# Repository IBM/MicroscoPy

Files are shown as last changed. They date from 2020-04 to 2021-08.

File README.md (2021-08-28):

# An open-source MICROSCOPE built using LEGO bricks, 3D-printing, Arduino and Raspberry Pi

Animation

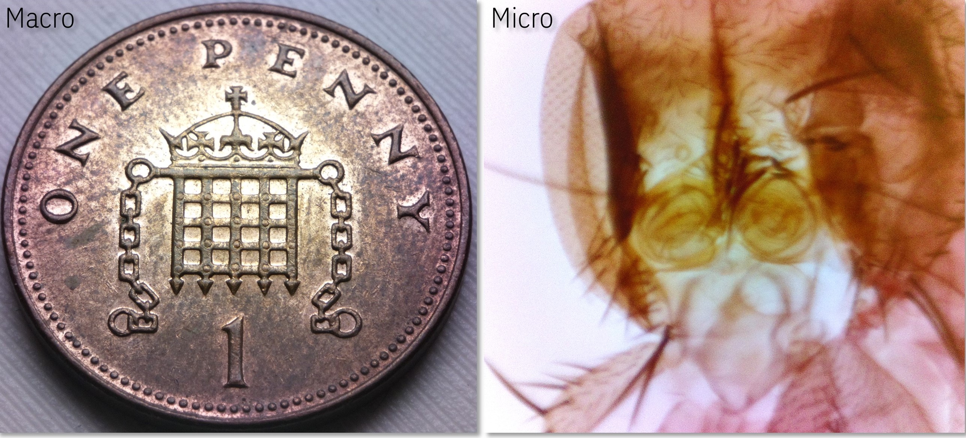
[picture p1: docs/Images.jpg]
Images


Stop-motion

## Key Features

- **Fully motorized:** Camera angle, sample position, magnification and focus can be adjusted precisely using six stepper motors.
- **Modular:** Stages and modules can be arranged in any configuration depending on the application.
- **Versatile:** Uniform illumination guarantees high quality imaging for a variety of samples with reflective or transparent surfaces.  
- **Wide magnification range:** Samples with features from several centimeters to several micrometers can be imaged without changing the objective lens.
- **Low-cost:** The whole assembly costs from $200 to $400 depending on the features and the vendors of the electronic components.  
- The microscope uses a **Raspberry Pi** mini-computer with an **8MP camera** to capture images and videos. Stepper motors and the illumination are controlled using a circuit board comprising an **Arduino microcontroller**, six **stepper motor drivers** and a **high-power LED driver**. All functions can be controlled from a keyboard connected to the Raspberry Pi or a separate custom-built Arduino joystick connected to the mainboard. **LEGO bricks** are used to construct the main body of the microscope to achieve a modular and easy-to-assemble design concept.

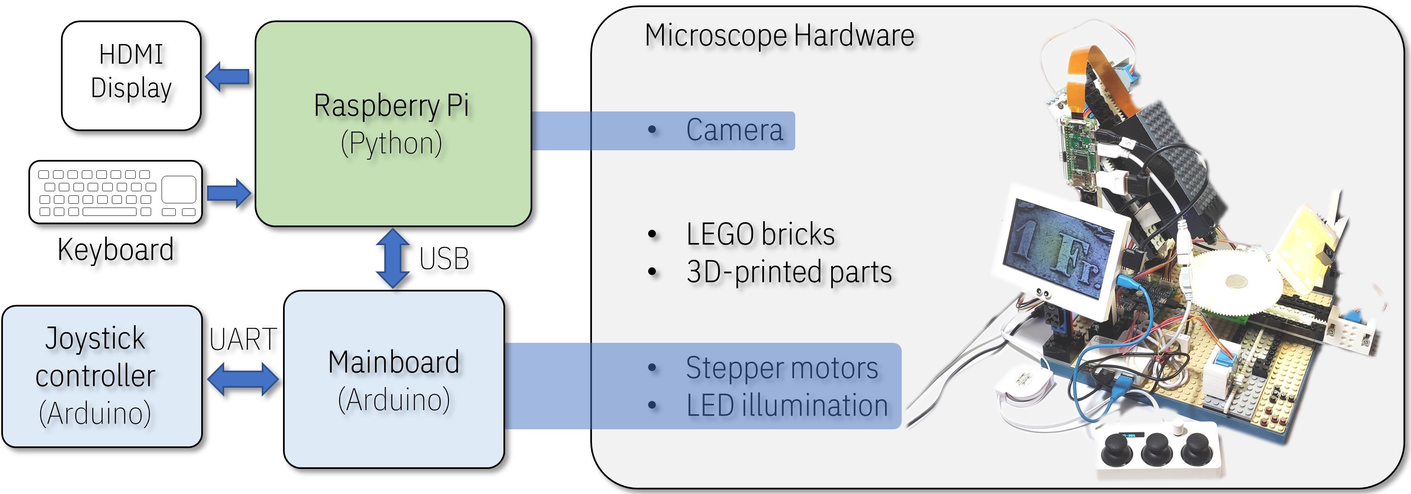
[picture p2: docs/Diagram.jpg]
Diagram


## Assembly instructions

|       [Video (YouTube)](https://youtu.be/PBSYnk9T4o4)        |     [Instructions (PDF)](Instructions.pdf)     |
| :----------------------------------------------------------: | :--------------------------------------------: |
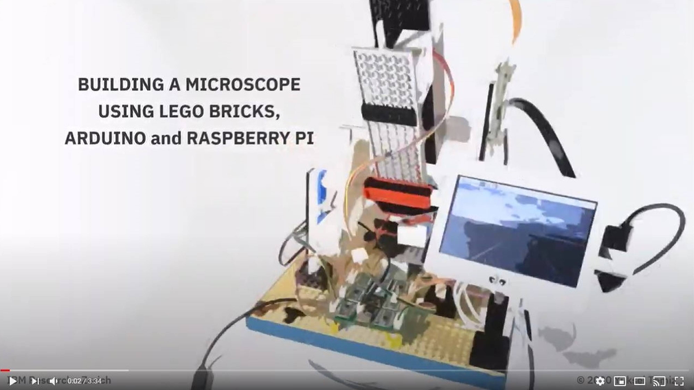
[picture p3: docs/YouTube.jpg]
YouTube (https://youtu.be/PBSYnk9T4o4)
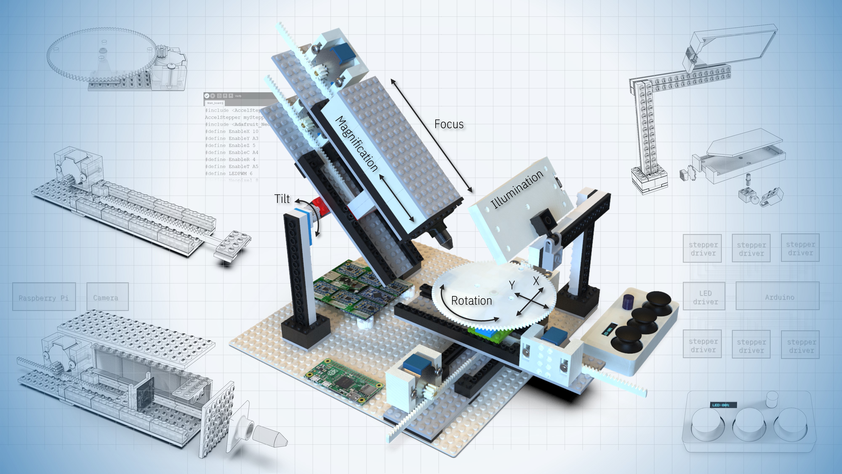
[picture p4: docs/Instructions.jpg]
|  |  |
|  **[Circuit assembly (PDF)](/Circuit/CircuitAssembly.pdf)**  | **[Raspberry Pi HQ camera test](/HQ-camera)**  |
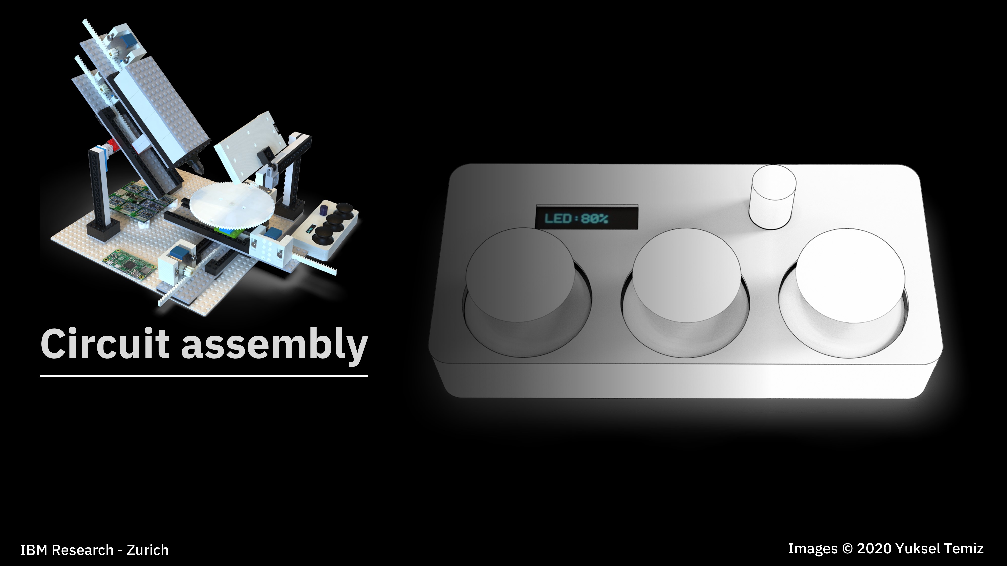
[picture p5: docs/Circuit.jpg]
Circuit
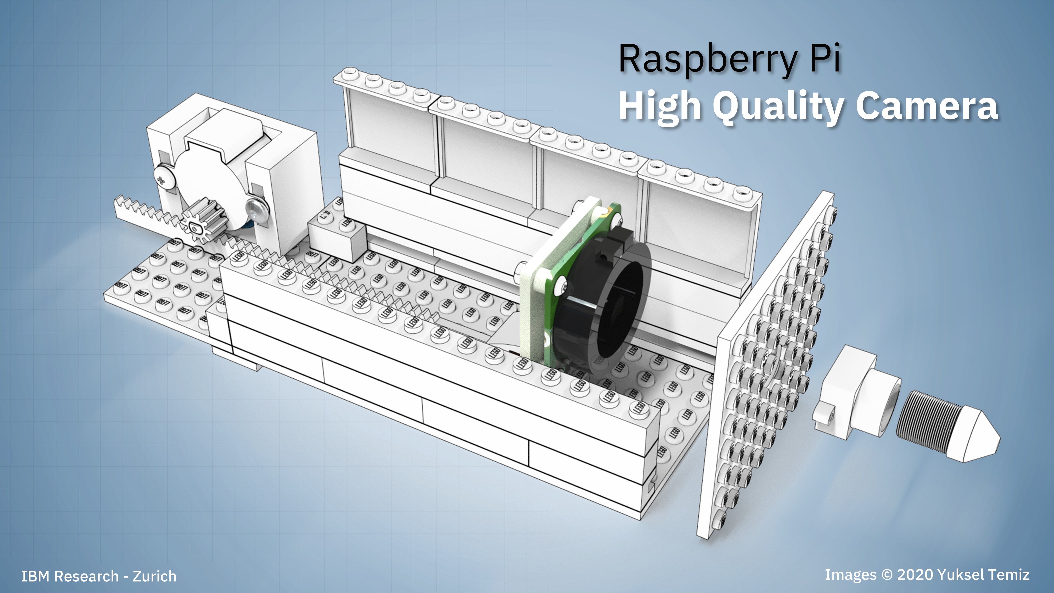
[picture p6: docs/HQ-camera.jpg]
HQ-camera
|  |  |

## Operation principle

The microscope has a simple operation principle based on changing the magnification and the focus by adjusting the relative distances between a **camera**, a single **objective lens** and a **sample**. Briefly, two linear stages with stepper motors are used to adjust these distances for a continuous and wide magnification range. Four additional stepper motors **tilt** the camera module and change the **X-Y position** and **rotation** of the sample. A **uniform light source** illuminates the sample either from an angle *(reflected light)* or from the bottom of the sample *(transmitted light)*. The system can also be used as a *digital water contact angle goniometer* by taking cross-section images of droplets. 

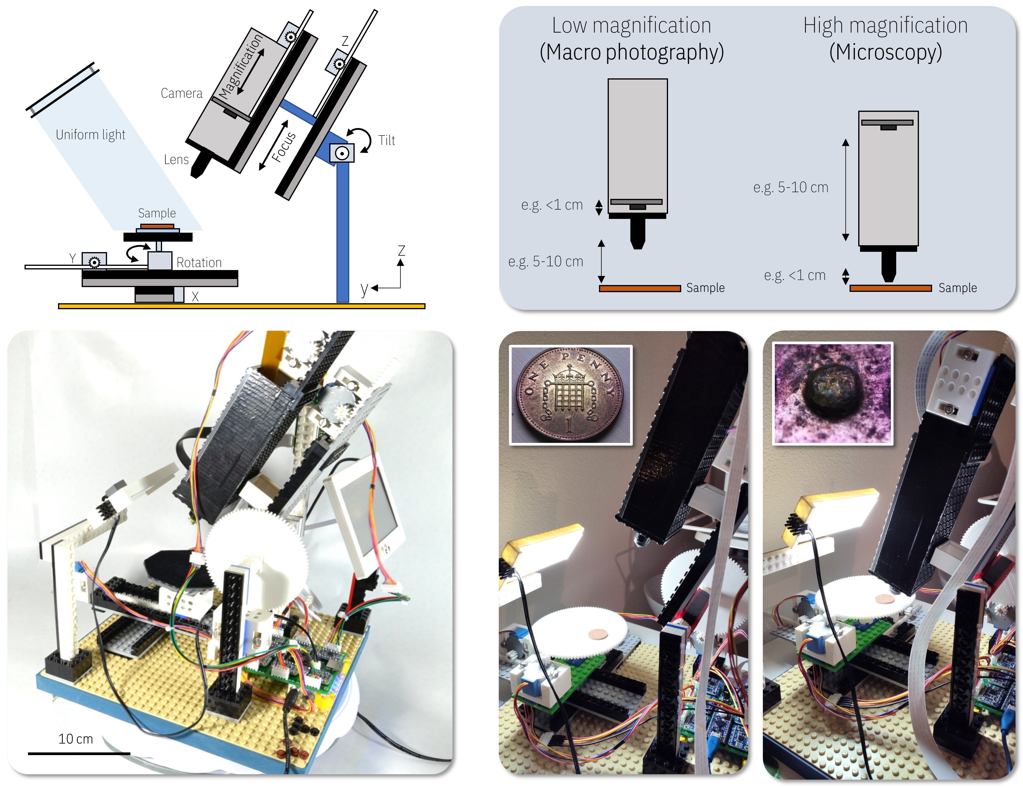
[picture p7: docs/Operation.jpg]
Operation


## Assembly steps

- [Enjoy the YouTube video and get a general idea about the assembly of the microscope.](https://youtu.be/PBSYnk9T4o4) 

- [Follow the detailed instructions provided in the PDF document.](Instructions.pdf)

- [3D print the design files.](#3D-printing)

- [Build the electronic board.](#Electronics)

- [Upload the Arduino code.](#Uploading-the-Arduino-code)

- [Assemble the microscope.](#Final-assembly)

- [Run the Python code.](#Python-Raspberry-Pi)

- [Try different operation modes and enjoy the microscope.](#Basic-operation-modes)

- [Check these instructions if you would like to test the new hiqh quality (HQ) camera](/HQ-camera)

## 3D printing

I assembled the main body of the microscope using individually-purchased [LEGO bricks](https://www.lego.com/en-us/page/static/pick-a-brick). Instead of using motors and gears from LEGO Technic, I designed custom actuators using [FreeCAD](https://www.freecadweb.org/) software and printed them using my personal [3D printer](https://www.creality3d.shop/products/creality3d-ender-3-pro-high-precision-3d-printer). This approach not only lowered the cost of the microscope but also gave me some flexibility in the design and implementation of precise linear and rotary actuators. In principle, the whole structure could be 3D-printed without using any LEGO parts but that would be less modular and more time consuming.  

All STL files for 3D printing and the original FreeCAD files for editing are available in this [folder](https://github.com/IBM/MicroscoPy/tree/master/3D-design-files). You may need to install [FreeCAD Gear workbench](https://wiki.freecadweb.org/Macro_FCGear) to edit the gears. 

:warning: A good quality printing depends on many factors. I optimized the designs after several iterations of printing. If the parts do not match well, some minor modification in the original design file (e.g. enlarging the holes matching to LEGO studs) or polishing/drilling may be required. More information on the printer and slicer settings is given in the [PDF document](Instructions.pdf) (page #72). 

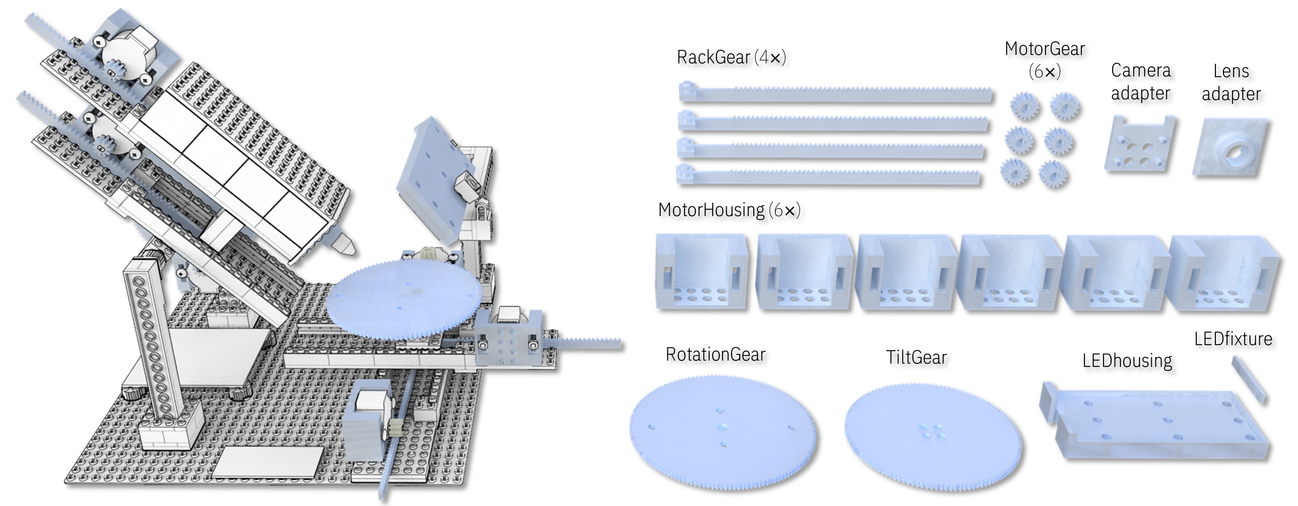
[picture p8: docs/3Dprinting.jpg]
3Dprinting


## Electronics  

:warning: **This part requires some basic knowledge on electronic circuit design and Arduino.**

All design and Gerber files of printed circuit boards (PCBs) are available in this [folder](/Circuit). I designed the PCBs using [DesignSpark PCB software](https://www.rs-online.com/designspark/pcb-software). The list of all components can be found in the [PDF document](Instructions.pdf) (page #71)  

There is also a separate [instruction manual](/Circuit/CircuitAssembly.pdf) giving more details about the assembly of the circuit boards.

The operation of the electronics is straight-forward. I used two Arduino microcontrollers, one for the *mainboard* (essential) and one for the joystick *controller* (optional), to control the stepper motors and the LED illumination of the microscope. In principle, everything could be controlled directly from the Raspberry Pi without using any Arduino microcontroller but I decided to leave testing this option for another time.

:bulb: The joystick controller is optional because the stepper motors and the LED can also be controlled from a keyboard connected to the Raspberry Pi. But having a joystick is fun!

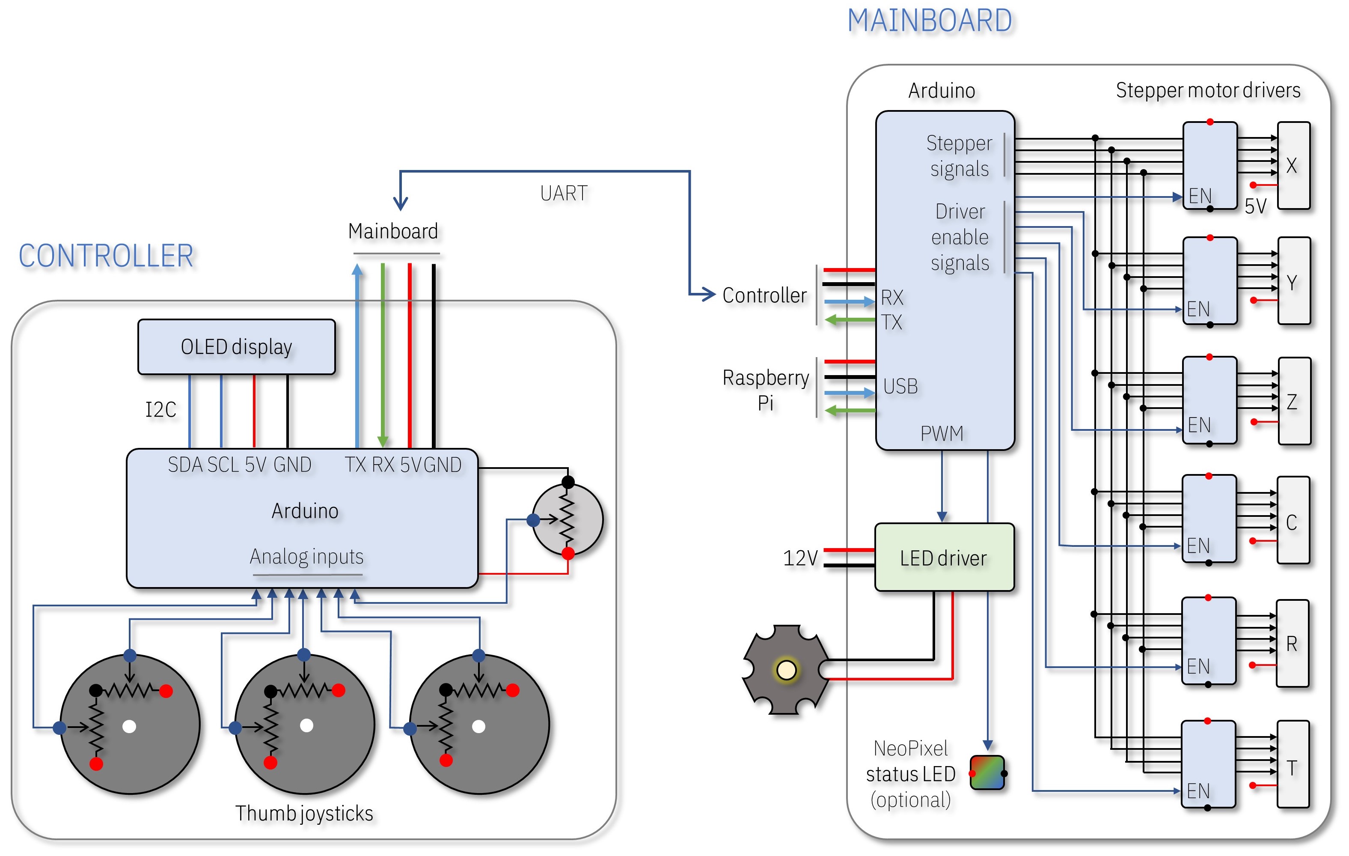
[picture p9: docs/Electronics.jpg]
Electronics


I preferred [Adafruit ItsyBitsy 32u4 5V](https://learn.adafruit.com/introducting-itsy-bitsy-32u4) but any Arduino board with enough number of I/O pins should work. If you want to use the joystick controller, the Arduino boards should support serial (UART) communication because they cannot communicate with each other via their USB ports. 

The Arduino on the *controller* circuit reads the status of three [thumb joysticks](https://www.sparkfun.com/products/9032) (for six stepper motors) and a potentiometer (for the LED intensity) via its analog inputs. The data is sent to the Arduino on the *mainboard* via UART (RX, TX) serial communication. An OLED display on the *controller* can be used to display useful information, like the PWM (pulse-width modulation) intensity of the LED. The Arduino on the *mainboard* receives and processes the incoming data and sends stepper motor signals to the corresponding stepper motor via its respective [motor driver](https://www.adafruit.com/product/3297). Six motor drivers share the same signal pins but only one driver is activated at a time using the *enable* *(EN)* or the *sleep* *(SLP)* pin of the driver. This implementation requires only 10 I/O pins *(4 signal + 6 enable)* instead of 24 *(4 signal x 6 motors)*. It also prevents the heating of the motors when they are idle and limits the current consumption by allowing only one motor running at a time. Alternatively, a motor driver with a built-in indexer with STEP/DIRECTION control can be used to reduce the number of I/O pins but such drivers are more expensive. The data is sent only if there is a change in the joystick position is detected to avoid continuous communication. 

The *mainboard* can be powered from an external 5V wall charger or directly from the USB port of the Raspberry Pi. The latter also allows USB communication between the *mainboard* and the Raspberry Pi to control the stepper motors and the LED intensity from a keyboard. The intensity of the LED is controlled by PWM using a dedicated pin on the Arduino. I recommend keeping the LED off while the Raspberry Pi is booting and then gradually increasing the intensity. The [LED driver](https://www.digikey.com/products/en?keywords=945-1818-5-ND) and the [high-power LED](https://www.digikey.com/products/en?keywords=1672-1161-ND) used in this project required more than 6V for a rated operation. I initially used an external 12V power adapter for the LED but later generated 12V directly from the USB port of the Raspberry Pi using a step-up [DC-DC converter](https://www.banggood.com/DC-DC-Boost-Buck-Adjustable-Step-Up-Step-Down-Automatic-Converter-XL6009-Module-p-1087346.html?rmmds=search&cur_warehouse=CN). In this case, the 5V power adapter should be able to supply enough current for the Raspberry Pi, stepper motors and the LED. I tested the system using a single 5V / 3A supply (original Raspberry Pi 4 power supply or a wall charger). Different configurations may require different power ratings. For example,  if the display is also powered from the same source, then a more powerful 5V source would be needed. [Here](https://www.digikey.com/products/en?keywords=709-GST60A05-P1J) is a good one.  

:warning: The high-power LED gets hot after some time, be cautious. I used a standard aluminum [heat sink](https://www.adafruit.com/product/3083) to help cooling a little bit.  

## Uploading the Arduino code 

- Download the latest version of the [Arduino IDE](https://www.arduino.cc/en/main/software) 
- Install the libraries (Sketch → Include Library → Manage Libraries):
  - [AccelStepper](http://www.airspayce.com/mikem/arduino/AccelStepper/): used to control the stepper motors (mainboard).
  - (Optional) [Adafruit NeoPixel](https://github.com/adafruit/Adafruit_NeoPixel): if you want to have a status LED or nice color effects in the mainboard.
  - (Optional) [Adafruit_GFX](https://github.com/adafruit/Adafruit-GFX-Library) and [Adafruit_SSD1306](https://github.com/adafruit/Adafruit_SSD1306): if you want to have an OLED display in the joystick to show the intensity of the LED illumination.
- Add the board by following these [instructions](https://learn.adafruit.com/introducting-itsy-bitsy-32u4/arduino-ide-setup). 
- Upload the [code(s)](/Arduino). 

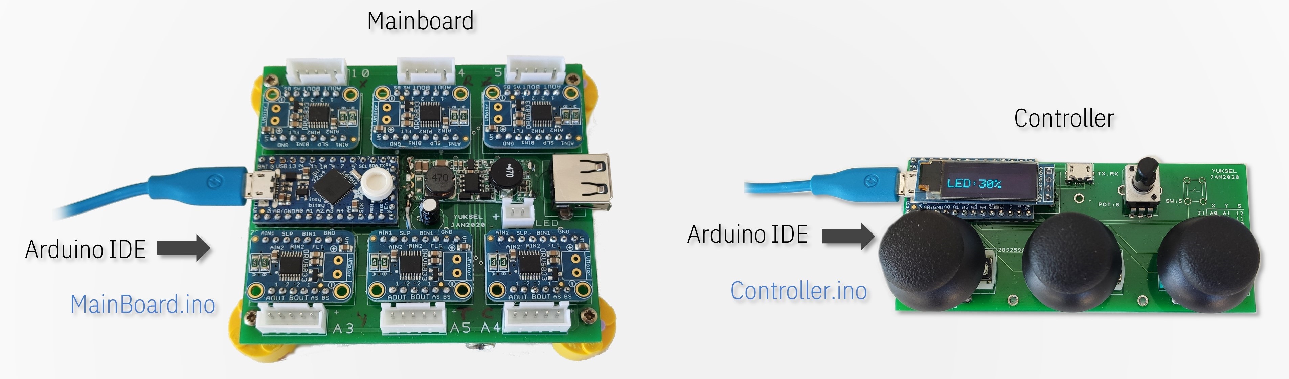
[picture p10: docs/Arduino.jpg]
Arduino


## Final assembly

Follow the detailed instructions given in the [PDF document](Instructions.pdf). Briefly:

- It is important to fix the [32x32 LEGO baseplate](https://www.lego.com/en-us/product/white-baseplate-11010) to a rigid table or support for a good mechanical stability. Rubber dampers or an air cushion can be used to minimize vibrations.  
- Unfortunately it is not possible to create a public shopping basket in the [LEGO shop](https://www.lego.com/en-us/page/static/pick-a-brick), all parts need to be added one by one. I listed the LEGO parts in [this document](List-of-Lego-bricks.pdf) but I recommend buying extra bricks and plates in case you need to change something. 
- Some LEGO parts are needed to be glued permanently for better stability. I provided recommendations in the document based on my experience. In general, it is a good idea to glue a smaller LEGO piece (e.g. 2x2) to a larger one (e.g. 2x4) to have a stronger interlocking while preserving the advantage of LEGO bricks for modularity. 
- After assembling the microscope and connecting all the cables, boot the Raspberry Pi. 
- :warning: Do not forget to enable the camera from the Raspberry Pi configuration (Preferences → Raspberry Pi configuration → Interfaces → Camera Enabled → Reboot)  as explained [here](https://projects.raspberrypi.org/en/projects/getting-started-with-picamera). 

Assembly

## Python-Raspberry Pi

I wrote a simple [program](/Python) in Python 3 to control the microscope, modify camera settings and take photos and videos from keyboard. The code allows changing almost all camera settings using keyboard shortcuts. The speed and the direction of the stepper motors and the LED intensity can also be controlled from the keyboard independently from the joystick controller.

The code requires following dependencies: 

- [EasyGUI](https://pythonhosted.org/easygui/index.html): to generate simple message boxes and select the folder where the images are saved
- [pySerial](https://pythonhosted.org/pyserial/): to communicate with the Arduino via USB
- [pynput](https://pypi.org/project/pynput/): to monitor keyboard inputs

There are two important parameters in the program to be changed according to your configuration:

**HighResolution:** 

- **True** for (3280x2464), tested with Raspberry Pi 4.
- **False** for (1920x1080), tested with Raspberry Pi 3 and Zero. 

**KeyboardControl:** 

- **True** if the Arduino mainboard is connected to the Raspberry Pi via USB.
- **False** if the mainboard is not connected and powered from an external 5V supply 

**Finally, launch the program from the terminal and enjoy the microscope:** 

```bash
python3 /home/pi/MicroscoPy.py 
```

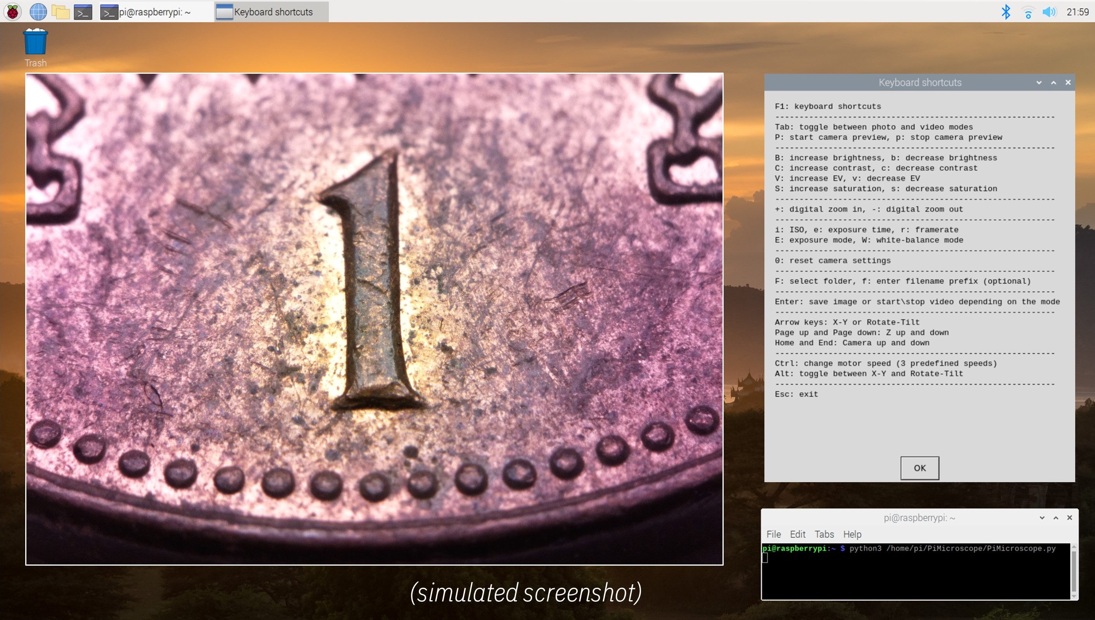
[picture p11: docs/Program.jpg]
Program


## Basic operation modes

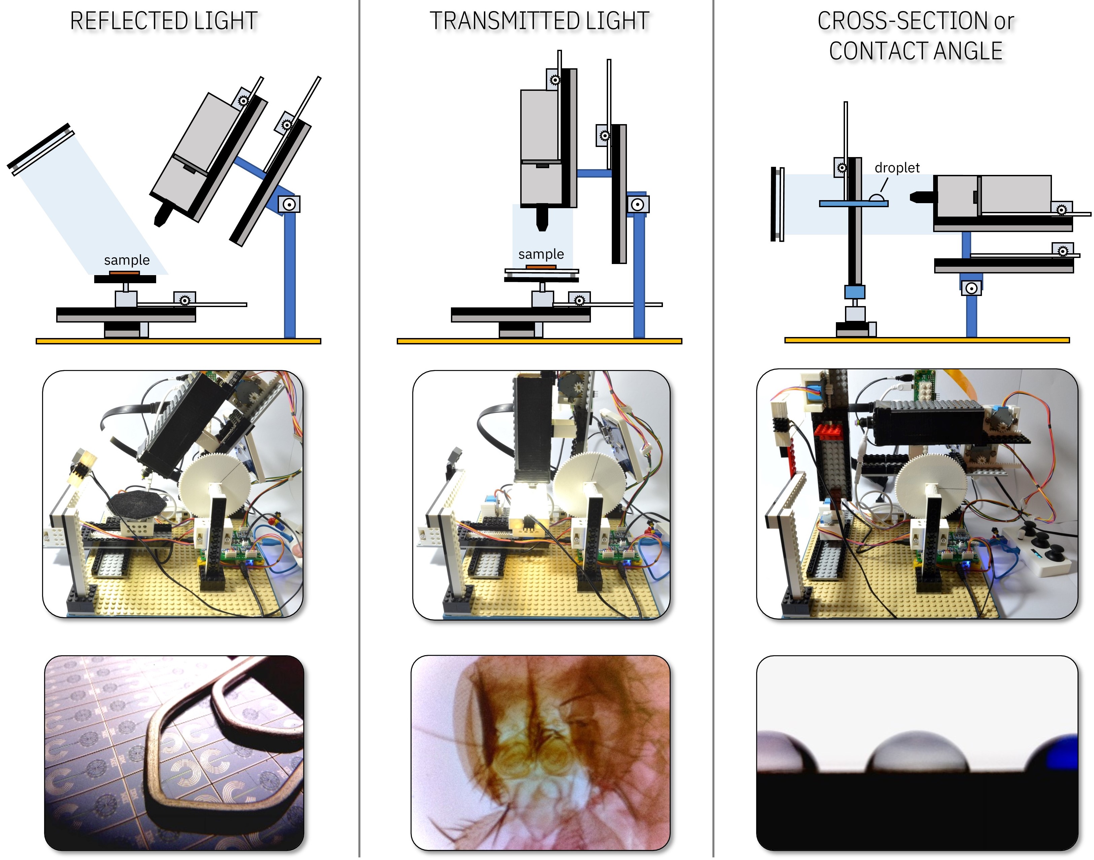
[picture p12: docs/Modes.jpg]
Modes


## Media coverage

[IEEE Spectrum](https://spectrum.ieee.org/geek-life/hands-on/build-a-sophisticated-microscope-using-lego-3d-printing-arduinos-and-a-raspberry-pi): "Build A Sophisticated Microscope Using Lego, 3D Printing, Arduinos, and a Raspberry Pi"

[IBM - Medium article](https://medium.com/@IBMResearch/ibm-open-sources-300-fully-functional-lego-microscope-design-248a6cdc81bf): "IBM open sources $300 fully-functional LEGO®microscope design"

[Futurism](https://futurism.com/engineer-published-scientific-papers-lego-microscope): "This Engineer Published Scientific Papers Using a Lego Microscope"

## License

This project uses the [Apache License Version 2.0](LICENSE) software license. 

Separate third-party libraries used in Arduino and Python codes are licensed by their respective providers pursuant to their own separate licenses. 

## About

**The microscope is not currently available for purchase in kit or built form.** 

Copyright 2021 [Yuksel Temiz](https://www.linkedin.com/in/yukseltemiz/)

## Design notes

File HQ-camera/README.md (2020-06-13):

# Raspberry Pi High Quality (HQ) camera test

This folder is dedicated to Raspberry Pi's new [HQ camera](https://www.raspberrypi.org/products/raspberry-pi-high-quality-camera/). 

The new camera gives a better quality imaging but it is 50% larger thus it requires a larger Lego housing, which challenges the tilting mechanism. The improvement is marginal for many cases because the performance of this microscope is anyway limited by other factors, like the low-cost objective lens. 

Overall, I think it is NOT worth the extra effort and cost unless a completely new microscope architecture with a more stable tilting mechanism and a better quality lens is designed.

Follow these detailed [instructions](Instructions_HQ.pdf) if you would like to try yourself. 

**Note:** Use the modified Python code (**MicroscoPy_HQ.py**) in this folder for the best resolution.

HQ-camera

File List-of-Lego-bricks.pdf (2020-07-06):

List of Lego bricks used in the prototypes.

Some bricks may not be available in your country, but there are always alternative implementations in the world of Lego bricks. Also, there are probably many different ways of building a similar or better modules than I designed.
So, use your imagination and order extra bricks from different kinds in case you may want to modify something.

Keep in mind that some parts are required to be glued to a bigger piece for better mechanical stability.

I appreciate if you also keep in mind that this is a research prototype originated from my hobby, not a product.
There are probably many things that could have been done better, so consider the documents as a guideline but not as a product manual. Please let me know if you spot an error or have suggestions for improvements.

### https://www.lego.com/en-us/page/static/pick-a-brick

Module | Lego design name | Lego design ID | Quantity per unit | Quantity total | Purpose | Page # in the instructions | Comments
Base | 1 unit
| Baseplate 32x32 | | 1 | 1 | base | 32 | needs to be fixed to a rigid substrate
Linear actuators | 4 units
| PLATE 6X16 | 3027 | 1 | 4 | main plate for the linear stage | 5
| SLIDING PIECE 1X4 | 2653 | 8 | 32 | sliding guides on the sides | 5
| PLATE 1X2 WITH SLIDE | 32028 | 2 | 8 | sliding pieces | 7
| PLATE 2X4 | 3020 | 1 | 4 | moving plate | 7
| PLATE 2x6 | 3795 | 1 | 4 | mechanical stability | 6
| PLATE 6x8 | 3036 | 1 | 4 | motor plate | 6
| BRICK CORNER 1X2X2 | 2357 | 2 | 8 | mechanical stability | 6
| PLATE 2X4 | 3020 | 1 | 4 | motor Lego adapter | 9
Camera module | 1 unit | | | | | | in addition to one linear stage
| WALL ELEMENT 1X4X3, ABS | 60581 | 8 | 8 | sidewalls | 18
| PLATE 6X16 | 3027 | 1 | 1 | top cover | 19
| ANGLE PLATE 1X2 / 2X4 | 21731 | 1 | 1 | top cover connection | 19
| ANGULAR PLATE 1.5 BOT. 1X2 2/2 | 99207 | 1 | 1 | camera Lego adapter | 15
| PLATE 6x6 | 3958 | 1 | 1 | front cover | 19
| FRAME 1X4X3 | 60594 | 2 | 2 | Camera-Z connection spacer | 58
| PLATE 2X4 | 3020 | 1 | 1 | Camera-Z connection spacer | 57
Rotaty stage (option 1) | 1 unit
| 10x10 OCTOGONAL PLATE | 89523 | 1 | 1 | stage | 25
| PROFILE BRICK Ø15.83 W. CROSS | 92947 | 1 | 1 | connection to the motor | 25
| PLATE 2X4 | 3020 | 1 | 1 | motor Lego adapter | 25
Rotaty stage (option 2) | 1 unit | | | | | | preferred, better precision
| PLATE 4X12 | 3029 | 1 | 1 | stage base | 26
| NOSE CONE SMALL 1X1 | 59900 | 1 | 1 | pivot | 26
| LIGHT SWORD - BLADE | 21462 | 1 | 1 | pivot rod | 26
| NOSE CONE 2X2X2 | 14918 | 1 | 1 | support for the rod | 26
| PLATE 2X4 | 3020 | 1 | 1 | mechanical stability | 26
| PLATE 2X4 | 3020 | 1 | 1 | motor Lego adapter | 25
Vertical supports | 3 units | | | | | | tilt mechanism and illumination
| BRICK 1X16 | 2465 | 2 | 6 | pillar | 30
| PLATE 2X16 | 4282 | 1 | 3 | pillar | 30
| FRAME PLATE 4X4 | 64799 | 1 | 3 | pillar support | 30
| ANGULAR PLATE 1.5 BOT. 1X2 2/2 | 99207 | 1 | 3 | connection | 30
| BRICK CORNER 1X2X2 | 2357 | 4 | 12 | connection | 30
| PLATE 1X4 | 3710 | 4 | 12 | connection | 30
| PLATE 1x2 | 3023 | 4 | 12 | connection | 30
Tilt mechanism | 1 unit
| TECHNIC BRICK 1X2, Ø4.9 | 3700 | 2 | 2 | camera stage | 31
| CONN.BUSH W.FRIC./CROSSALE | 43093 | 2 | 2 | camera stage | 31
| PLATE 2X8 | 3034 | 2 | 2 | camera stage | 31
| BRICK 2X6 | 44237 | 1 | 1 | camera stage | 31
| PLATE 2X4 | 3020 | 3 | 3 | mechanical stability | 34-37
| PLATE 2X4 | 3020 | 1 | 1 | motor Lego adapter | 34-37
| PROFILE BRICK Ø15.83 W. CROSS | 92947 | 5 | 5 | spacer | 34-37
| TURN PLATE 2X2, LOWER PART | 3680 | 2 | 2 | rotation | 34-37
| TURN PLATE 2X2, UPPER PART | 3679 | 2 | 2 | rotation | 34-37
Illumination | 1 unit | | | | | | in addition to one vertical support
| CONN.BUSH W.FRIC./CROSSALE | 43093 | 4 | 4 | connection to the stage | 42-44 | for bottom illumination
| BRICK 1X16 | 2465 | 2 | 2 | horizontal connection | 43
| PLATE 2X16 | 4282 | 1 | 1 | horizontal connection | 43
| BRICK 2X2 W. BALL Ø 10.2 | 57909 | 1 | 1 | hinge | 43 | for top illumination
| BRICK 2X2 W. CUP FOR BALL | 92013 | 1 | 1 | hinge | 43 | for top illumination

OPTIONAL
HQ camera (experimental) | 1 unit | | | | | | Optional. Refer to the Instructions_HQ.pdf
linear actuator | PLATE 8x16 | 92438 | 1 | 1 | main plate | 4
linear actuator | PLATE 6x8 | 3036 | 1 | 1 | motor plate | 4
linear actuator | PLATE 2x8 | 3034 | 1 | 1 | mechanical stability | 4
linear actuator | PLATE 2x6 | 3795 | 1 | 1 | moving plate | 4 | same as camera v2
linear actuator | PLATE 1X2 WITH SLIDE | 32028 | 2 | 2 | sliding pieces | 4 | same as camera v2
linear actuator | BRICK CORNER 1X2X2 | 2357 | 2 | 2 | mechanical stability | 4 | same as camera v2
linear actuator | PLATE 2X4 | 3020 | 1 | 1 | motor Lego adapter | 4 | same as camera v2
linear actuator | SLIDING PIECE 1X4 | 2653 | 8 | 8 | sliding guides on the sides | 4 | same as camera v2
camera module | ANGULAR PLATE 1.5 BOT. 1X2 2/2 | 99207 | 1 | 1 | camera Lego adapter | 6 | same as camera v2
camera module | PLATE W. BOW 2X2X2/3 | 15068 | 1 | 1 | mechanical stability | 7
camera module | WALL ELEMENT 1X4X3, ABS | 60581 | 8 | 8 | sidewalls | 9 | same as camera v2
camera module | BRICK 1X16 | 2465 | 4 | 4 | additional height | 9
camera module | ANGLE PLATE 1X2 / 2X4 | 21731 | 1 | 1 | top cover connection | 10 | same as camera v2
camera module | PLATE 8X16 | 92438 | 1 | 1 | top cover | 10
camera module | PLATE 8X8 | 41539 | 1 | 1 | front cover | 10
tilt mechanism | PLATE 4X8 | 3035 | 2 | 2 | camera stage top and bottom plate | 13 | wider stage
tilt mechanism | TECHNIC BRICK 1X2, Ø4.9 | 3700 | 2 | 2 | camera stage | 13 | same as camera v2
tilt mechanism | CONN.BUSH W.FRIC./CROSSALE | 43093 | 2 | 2 | camera stage | 13 | same as camera v2
tilt mechanism | BRICK 1X8 | 3008 | 2 | 2 | camera stage | 13
tilt mechanism | PLATE 2X6 | 3795 | 1 | 1 | camera stage | 13

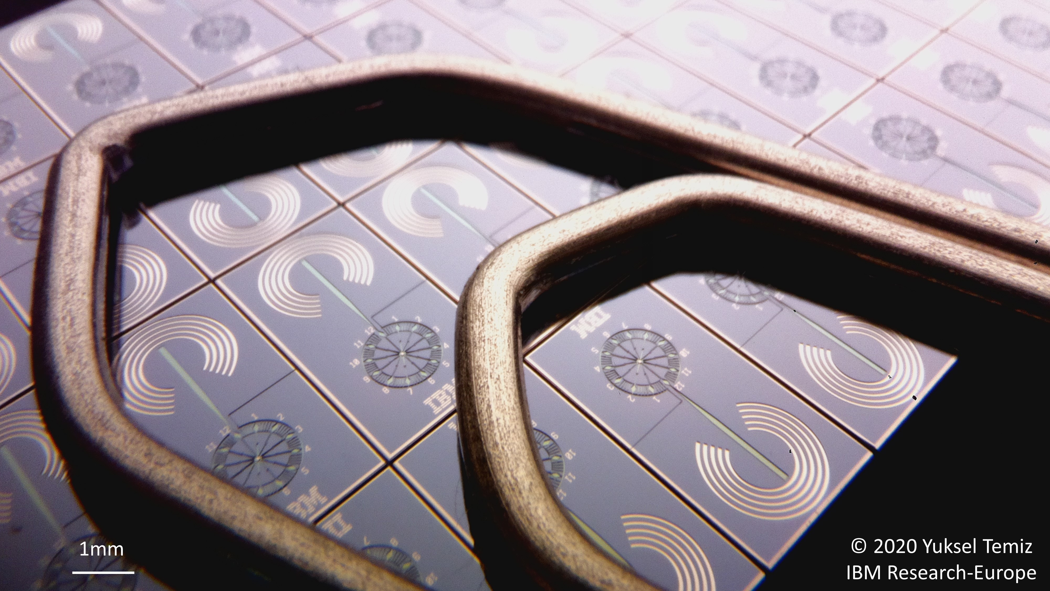
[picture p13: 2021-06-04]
Image-examples/Microfluidic-clock_and_paper-clip.jpg

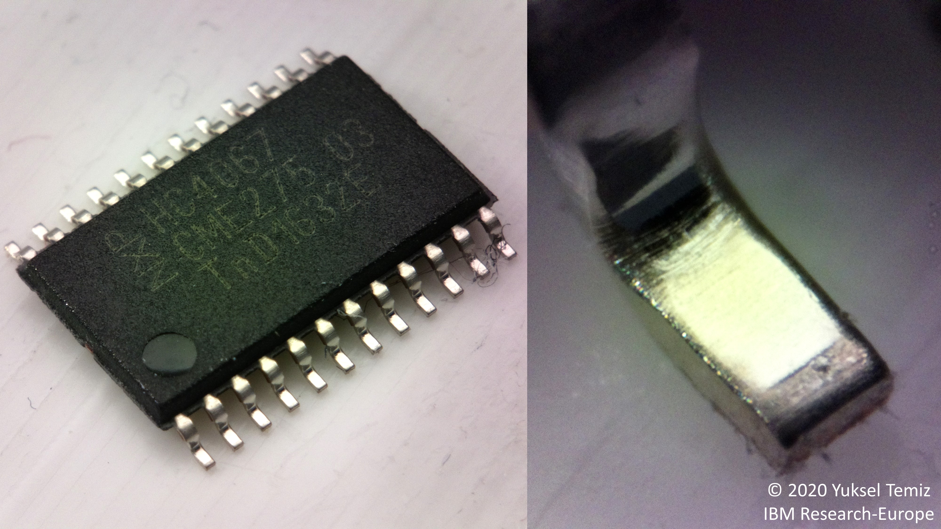
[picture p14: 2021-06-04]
Image-examples/Integrated-Circuit.jpg

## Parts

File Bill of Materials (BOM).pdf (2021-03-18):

# Bill of materials

I tem | Total price ($) | Remarks
LEGO bricks (https://www.lego.com/en-us/page/static/pick-a-brick) | ~60 | I recommend buying extra bricks in different sizes.
Raspberry Pi (https://www.raspberrypi.org/products/) | 10-50 | Any model works.
Raspberry Pi camera (https://www.raspberrypi.org/products/camera-module-v2/) | 25
Camera flex cable (https://www.adafruit.com/product/1731) | 3 | A long cable (>40cm) is preferred if the Raspberry Pi cannot be placed closer to the camera.
Magnifying lens (https://www.aliexpress.com/i/32879460954.html) | 10 | M12 thread
Micro SD card (https://www.raspberrypi.org/documentation/installation/sd-cards.md) | 10 | Raspberry Pi operating system. Minimum 16GB is recommended.
HDMI display (https://www.adafruit.com/product/2260) | 50-150 | Optional if an HDMI display is already available. The price varies depending on the size and the model.
Arduino board (https://www.adafruit.com/product/3677) x2 | 20 | One for the mainboard, one for the controller. Any Arduino board with enough number of IO pins should work.
Stepper motor driver (https://www.adafruit.com/product/3297) x6 | 30 | Any other 5V compatible driver should work. Microstepping was not needed in this project.
Stepper motor (https://www.banggood.com/28BYJ-48-5V-4-Phase-DC-Gear-Stepper-Motor-DIY-Kit-p-1553617.html?rmmds=search&cur_warehouse=CN) x6 | 15 | 28BYJ-48, 5V, 1/64 gear ratio
JST-XH 5P 4S cables (https://www.ebay.com/itm/JST-XH-5P-4S-Li-PO-Balance-Charging-Wire-Extension-22AWG-20cm-Adapter-Lead-x-5/122329707748) | 7 | A few of these cables are required the extend the default cable of the stepper motor (28BYJ-48)
High-power LED (https://www.digikey.com/products/en?keywords=1672-1161-ND) | 4
High-power LED driver (https://www.digikey.com/products/en?keywords=945-1818-5-ND) | 14
Light diffuser (https://www.adafruit.com/product/1621) | 3 | An LED backlight module is modified by replacing the low-power LED by a high-power one
Potentiometer (https://www.adafruit.com/product/4133) | 1 | LED intensity control using pulse-width modulation.
Thumb joysticks (https://www.sparkfun.com/products/9032) x3 | 12 | Three joysticks for X, Y, Z, Camera, Tilt, and Rotation.
5V power supply (https://www.raspberrypi.org/products/type-c-power-supply/) | 20 | At least 3A is preferred. A more powerful supply may be needed if the display is also powered from the same supply.
DC-DC converter for the LED (https://www.banggood.com/USB-Boost-Line-Power-Supply-5V-To-12V-Power-Line-1A-Power-Cord-p-1268454.html) | 3 | 5V to 12V converter for the LED (note: I do not recommend using Raspberry Pi’s USB output for the LED, you can use a separate 12V power supply or use this converter with a standard 5V phone charger)
DC barrel connector (LED) (https://www.digikey.com/en/products/detail/cui-devices/PJ-002A/96962?s=N4IgTCBcDaIMYAcC0AGFYCGSB2ATEAugL5A) | 1 | Connector for the 12V input (LED)
OLED display (https://www.banggood.com/0_91-Inch-128x32-IIC-I2C-Blue-OLED-LCD-Display-DIY-Oled-Module-SSD1306-Driver-IC-DC-3_3V-5V-p-1140506.html?rmmds=search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) | 3 | Displays the LED intensity or any other information on the controller.
USB connector (https://www.digikey.com/products/en?keywords=UE27AC5410H-ND) (type A) | 0.5 | Connection between the mainboard and the controller (mainboard side).
USB connector (https://www.digikey.com/products/en?keywords=609-4616-1-ND) (micro) | 0.5 | Connection between the mainboard and the controller (controller side).
JST XH connector set (https://www.banggood.com/40-Sets-JST-2_5mm-XH-2P-3P-4P-5Pin-Male-Female-Housing-Connector-with-Crimps-p-1180083.html?rmmds=search&cur_warehouse=CN) | 5 | Connectors for the stepper motors and the LED
OVERALL TOTAL | ~300

## - The prices and the links are for exemplary components that

were used in this prototype.

## - Any other compatible model

should work in principle.

## - The total price varies significantly depending on the vendor and the model. For example, the type of the Raspberry Pi and the display makes a big difference in the

price.

## - The cost of 3D-printed parts is

not included.

## - There are also a few other accessories needed, like USB

cables, an HDMI cable,

## optionally a mouse and a

keyboard, an ON/OFF switch,

## screws and nuts, and printed

circuit boards (PCBs).

IBM Research - Zurich | Images © 2020 Yuksel Temiz

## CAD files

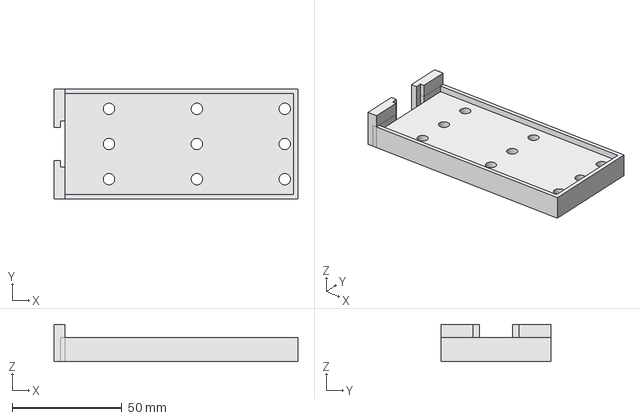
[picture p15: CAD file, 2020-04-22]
3D-design-files/FreeCAD/9-LEDhousing.FCStd
111.0 x 50.0 x 17.0 mm

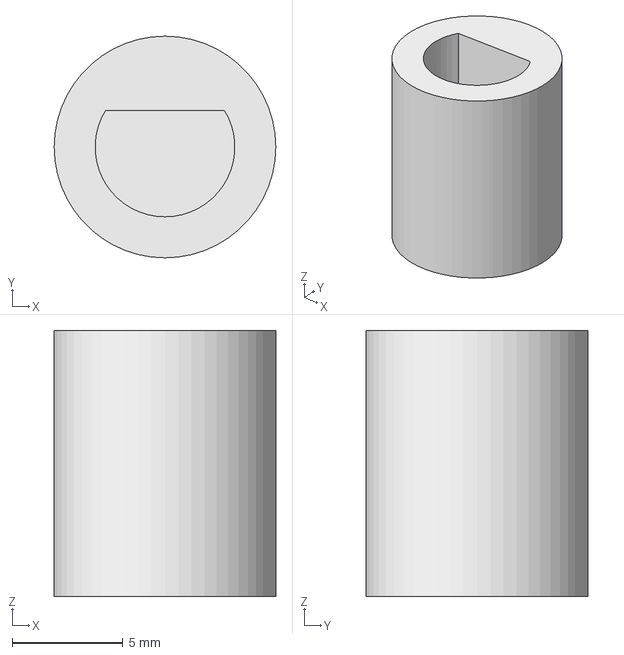
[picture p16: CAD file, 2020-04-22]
3D-design-files/FreeCAD/Joystick Controller/Controller knob.FCStd
10.0 x 10.0 x 12.0 mm

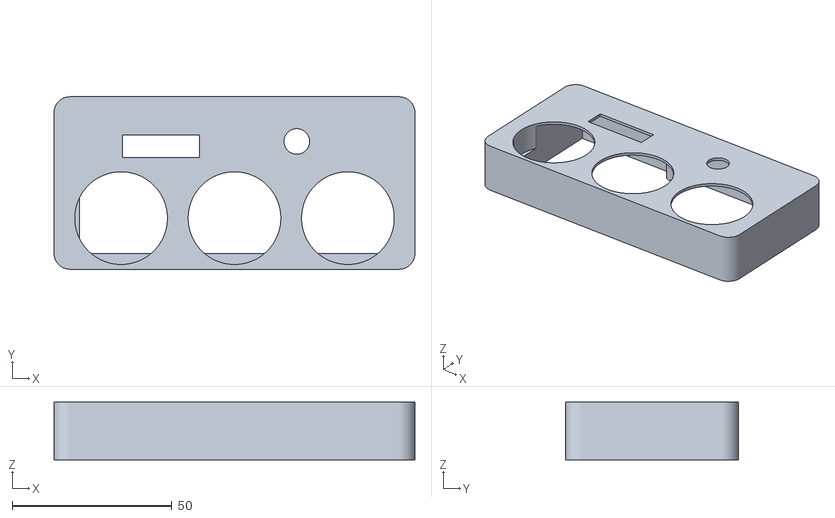
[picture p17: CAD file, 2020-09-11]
3D-design-files/STL/11-ControllerHousing.stl
113.0 x 54.0 x 18.0

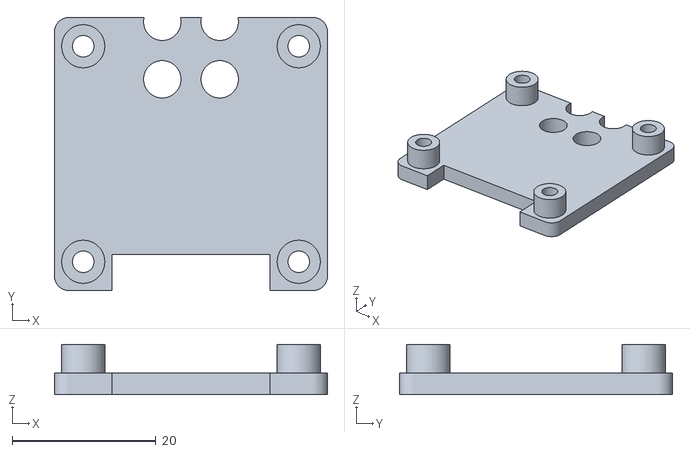
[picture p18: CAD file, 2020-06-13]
HQ-camera/CameraAdapter_HQ.stl
38.0 x 38.0 x 7.00

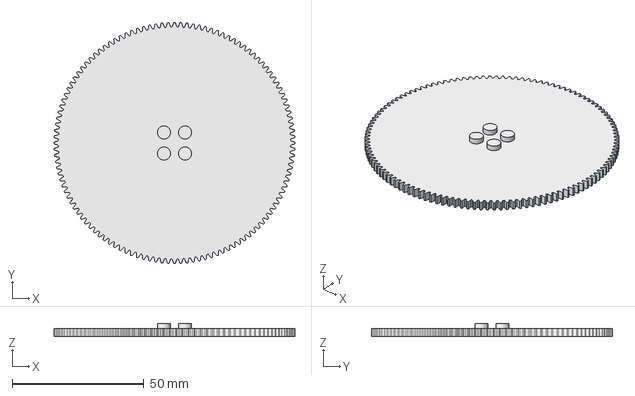
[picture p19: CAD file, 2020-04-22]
3D-design-files/FreeCAD/8-TiltGear.FCStd
91.5 x 91.5 x 4.90 mm

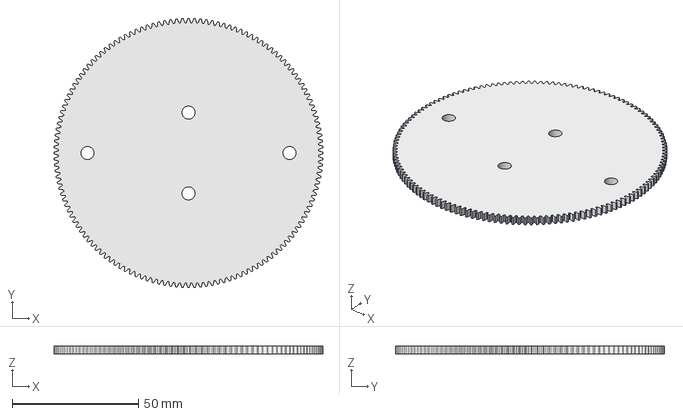
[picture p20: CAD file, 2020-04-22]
3D-design-files/FreeCAD/7-RotationGear.FCStd
106.5 x 106.5 x 3.00 mm

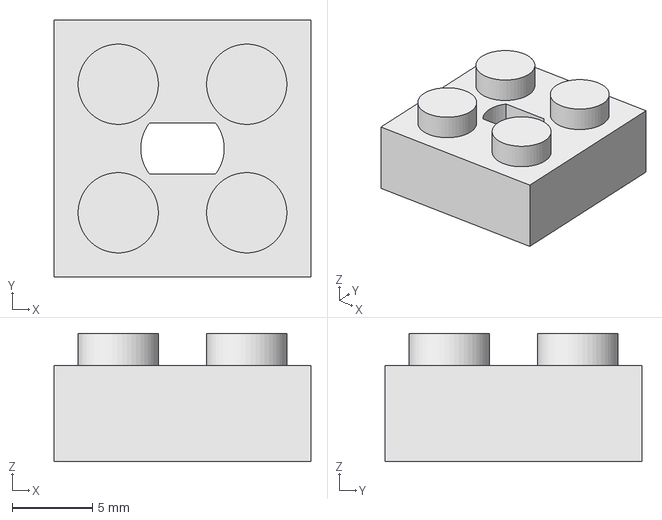
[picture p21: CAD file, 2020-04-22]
3D-design-files/FreeCAD/6-ShaftAdapter.FCStd
16.0 x 16.0 x 8.00 mm

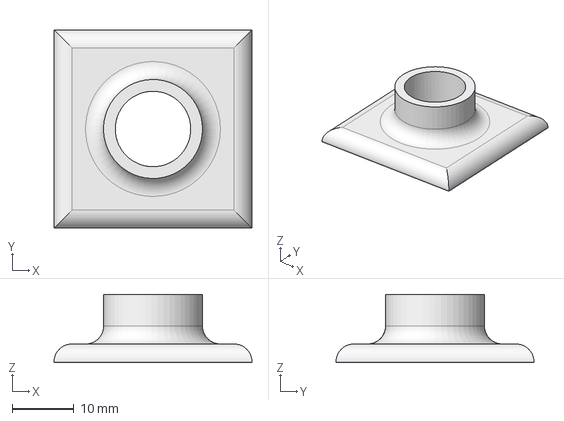
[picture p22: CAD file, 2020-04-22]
3D-design-files/FreeCAD/5-LensAdapter.FCStd
32.0 x 32.0 x 11.0 mm

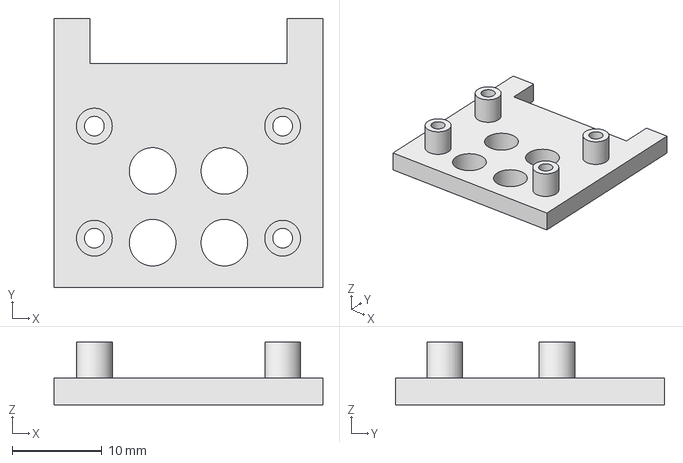
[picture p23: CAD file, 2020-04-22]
3D-design-files/FreeCAD/4-CameraAdapter.FCStd
30.0 x 30.0 x 7.00 mm

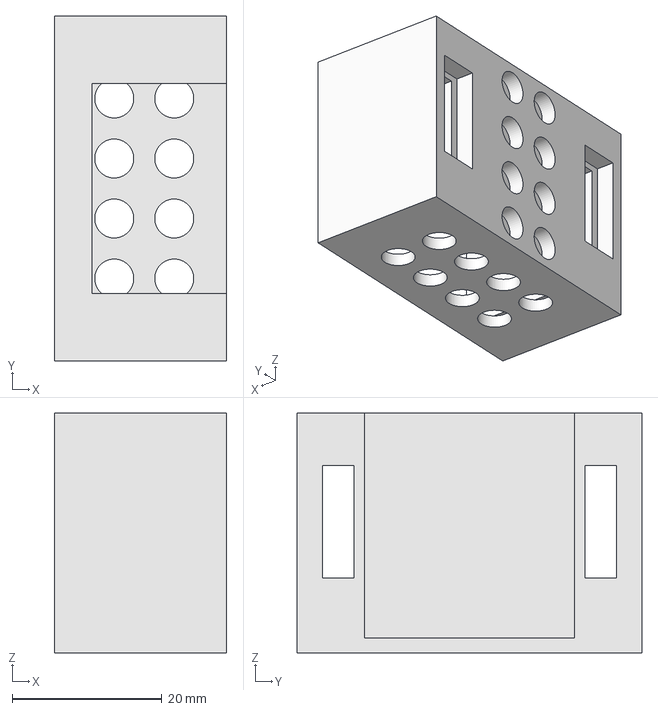
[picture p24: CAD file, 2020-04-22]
3D-design-files/FreeCAD/3-MotorHousing.FCStd
23.0 x 46.0 x 32.0 mm

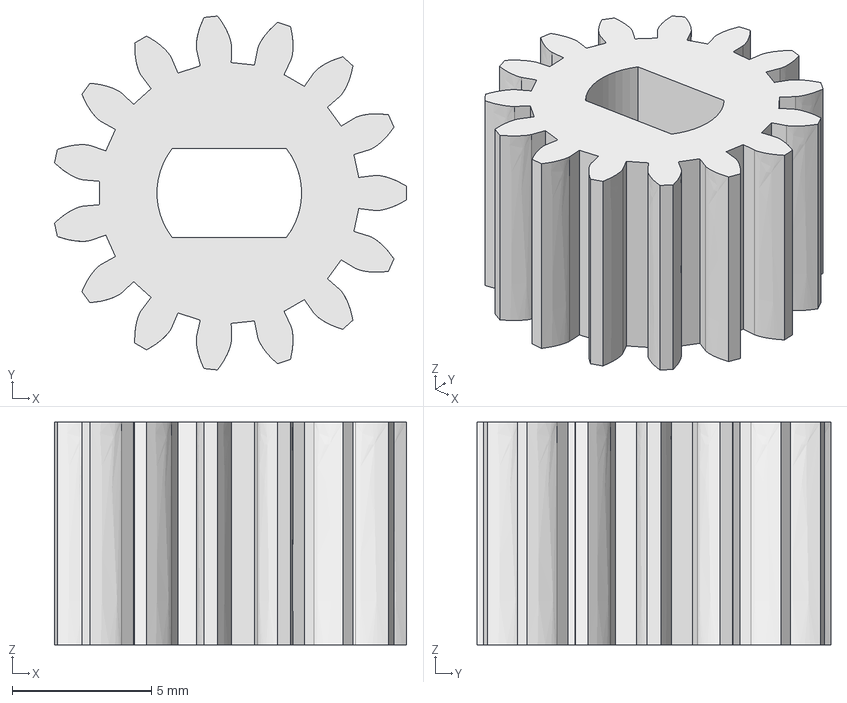
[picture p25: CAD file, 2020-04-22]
3D-design-files/FreeCAD/2-MotorGear.FCStd
12.7 x 12.7 x 8.00 mm

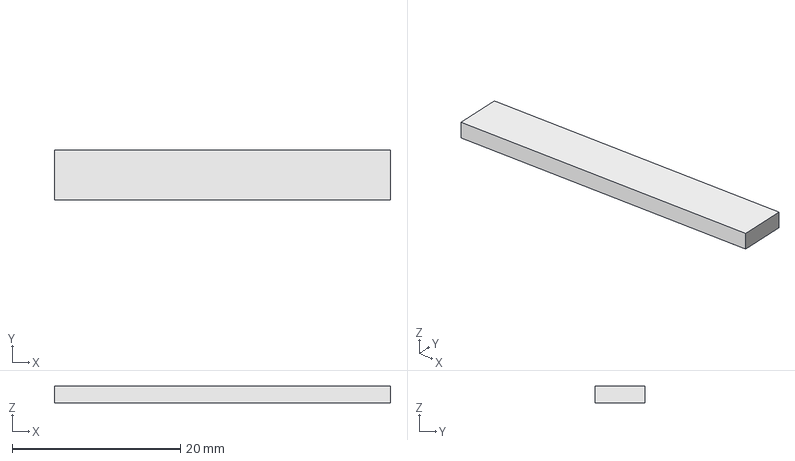
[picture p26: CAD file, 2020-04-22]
3D-design-files/FreeCAD/10-LEDfixture.FCStd
40.0 x 6.00 x 2.00 mm

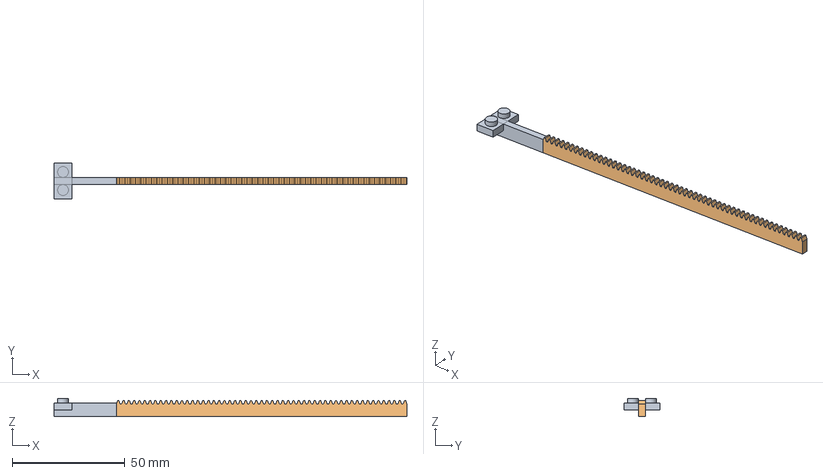
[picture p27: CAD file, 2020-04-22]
3D-design-files/FreeCAD/1-RackGear.FCStd
156.6 x 16.0 x 8.00 mm
InvoluteRack

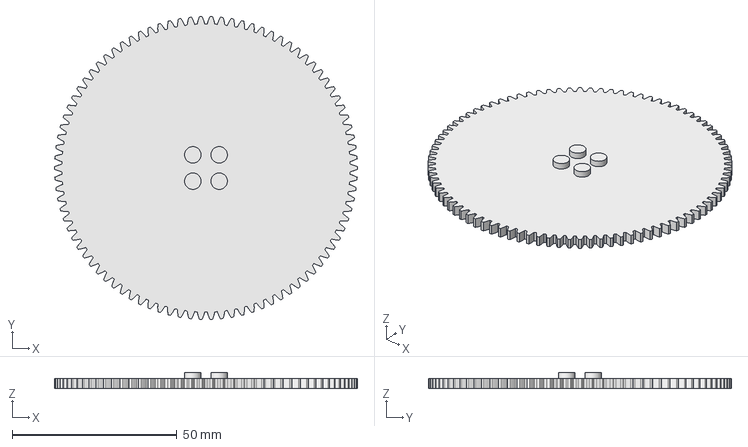
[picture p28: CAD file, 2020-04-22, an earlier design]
3D-design-files/FreeCAD/Legacy designs/TiltGear_legacy.FCStd
92.0 x 92.0 x 4.90 mm

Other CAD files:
3D-design-files/FreeCAD/Joystick Controller/Controller housing.FCStd
3D-design-files/STL/12-ControllerKnob.stl
3D-design-files/FreeCAD/Legacy designs/RotationGear_legacy.FCStd
3D-design-files/FreeCAD/Legacy designs/RackGear_legacy.FCStd
3D-design-files/FreeCAD/Legacy designs/MotorGear_legacy.FCStd
3D-design-files/STL/1-RackGear.stl
3D-design-files/STL/10-LEDfixture.stl
3D-design-files/STL/2-MotorGear.stl
3D-design-files/STL/3-MotorHousing.stl
3D-design-files/STL/4-CameraAdapter.stl
3D-design-files/STL/5-LensAdapter.stl
3D-design-files/STL/6-ShaftAdapter.stl
3D-design-files/STL/7-RotationGear.stl
3D-design-files/STL/8-TiltGear.stl
3D-design-files/STL/9-LEDhousing.stl

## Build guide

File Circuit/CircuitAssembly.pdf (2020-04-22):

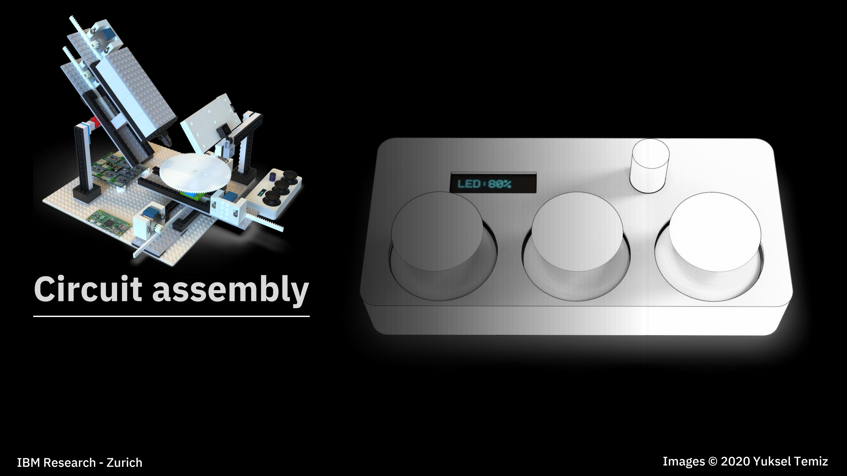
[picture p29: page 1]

# Circuit assembly

IBM Research - Zurich | Images © 2020 Yuksel Temiz

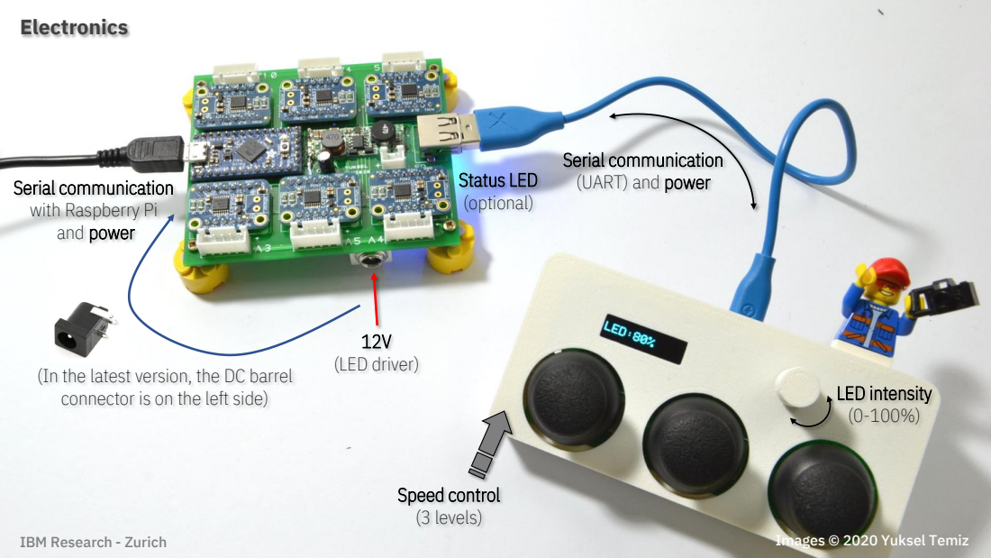
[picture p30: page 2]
Electronics; 12V (LED driver); Speed control (3 levels); LED intensity (0-100%); Status LED (optional)

Serial communication
(UART) and power

with Raspberry Pi
and power

(In the latest version, the DC barrel
connector is on the left side)

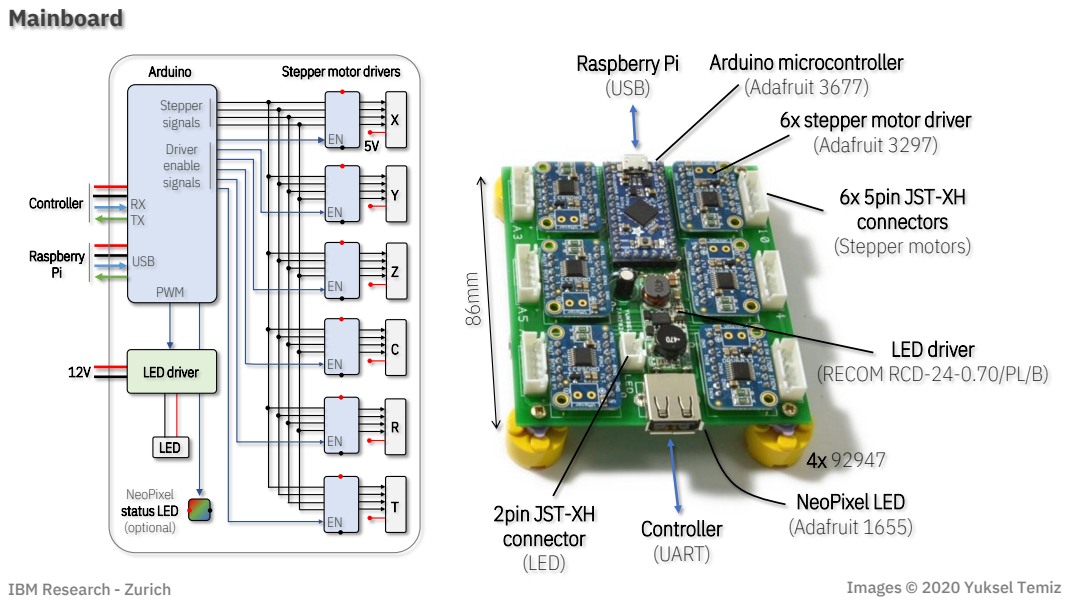
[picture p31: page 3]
Mainboard; 6x 5pin JST-XH connectors (Stepper motors); LED driver; Controller (UART); 2pin JST-XH connector (LED); NeoPixel LED (Adafruit 1655); Controller; Raspberry Pi; LED; Stepper signals; Driver enable signals; Arduino; USB; PWM; NeoPixel status LED (optional); Raspberry Pi (USB)

Arduino microcontroller
(Adafruit 3677)
6x stepper motor driver
(Adafruit 3297)

Stepper motor drivers

(RECOM RCD-24-0.70/PL/B)

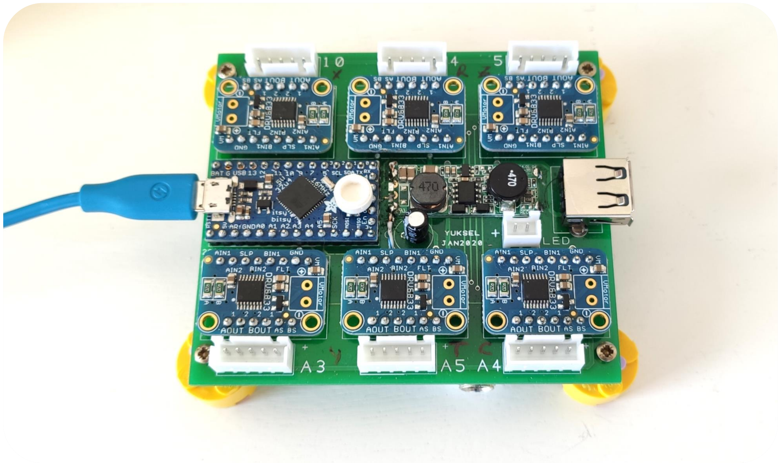
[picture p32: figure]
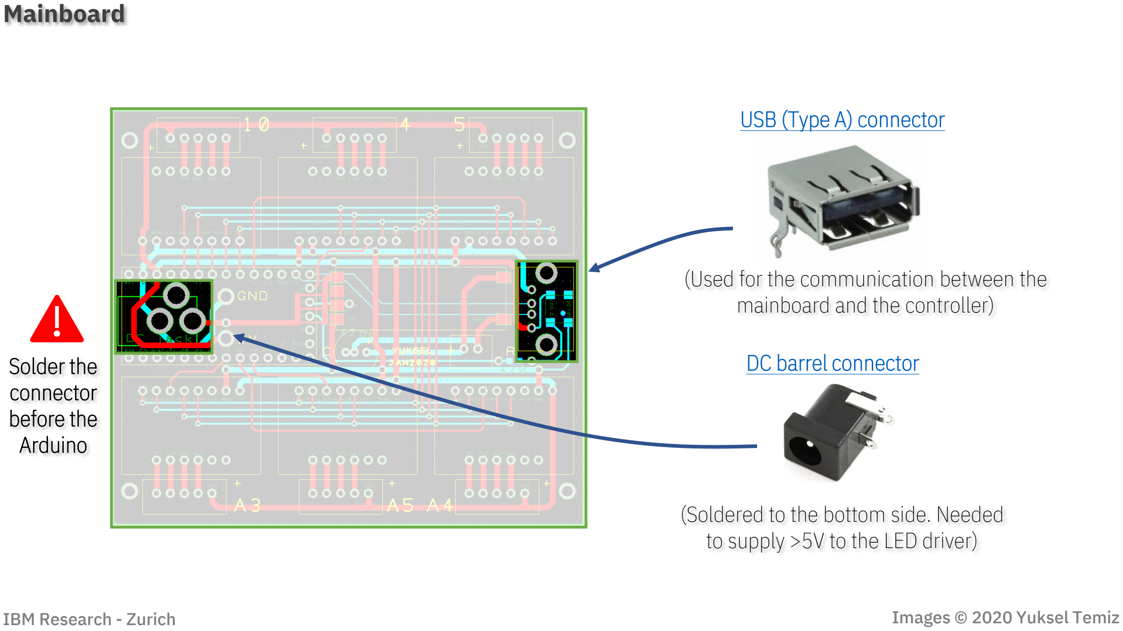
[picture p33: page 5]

(Used for the communication between the mainboard and the controller)

USB (Type A) connector (https://www.digikey.com/products/en?keywords=UE27AC5410H-ND)

DC barrel connector (https://www.sparkfun.com/products/119)

(Soldered to the bottom side. Needed to supply >5V to the LED driver)

Solder the
connector
before the
Arduino

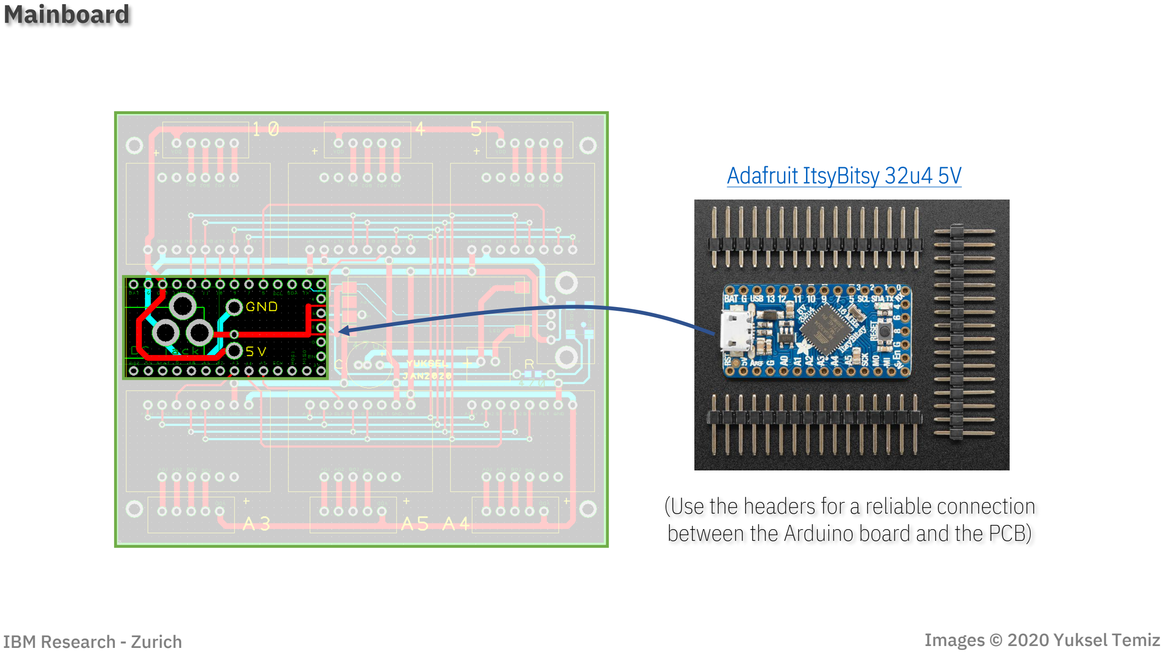
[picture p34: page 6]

Adafruit ItsyBitsy 32u4 5V (https://www.adafruit.com/product/3677)

(Use the headers for a reliable connection between the Arduino board and the PCB)

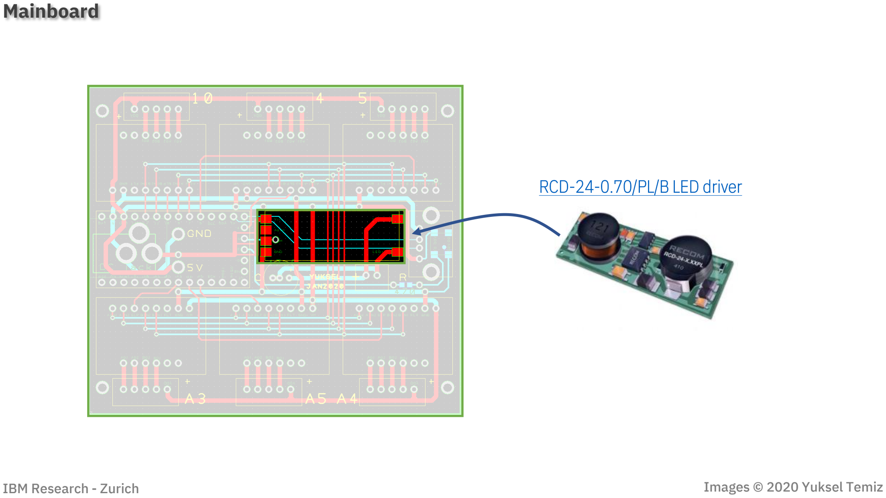
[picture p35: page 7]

RCD-24-0.70/PL/B LED driver (https://www.digikey.com/products/en?keywords=945-1818-5-ND)

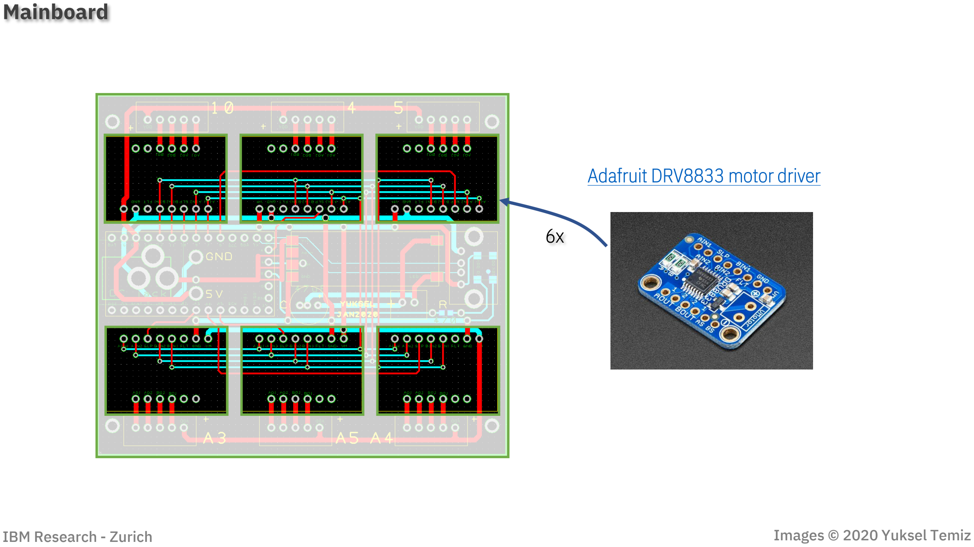
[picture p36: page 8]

Adafruit DRV8833 motor driver (https://www.adafruit.com/product/3297)

6x

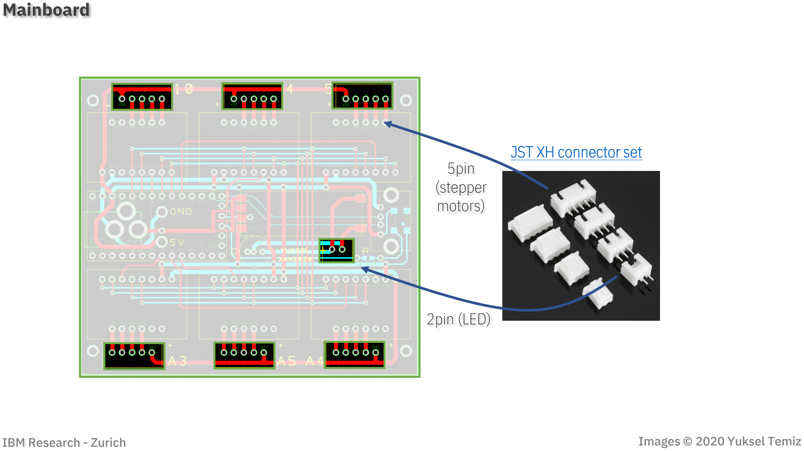
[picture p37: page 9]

JST XH connector set (https://www.banggood.com/40-Sets-JST-2_5mm-XH-2P-3P-4P-5Pin-Male-Female-Housing-Connector-with-Crimps-p-1180083.html?rmmds=myorder&cur_warehouse=CN)
5pin
(stepper
motors)

2pin (LED)

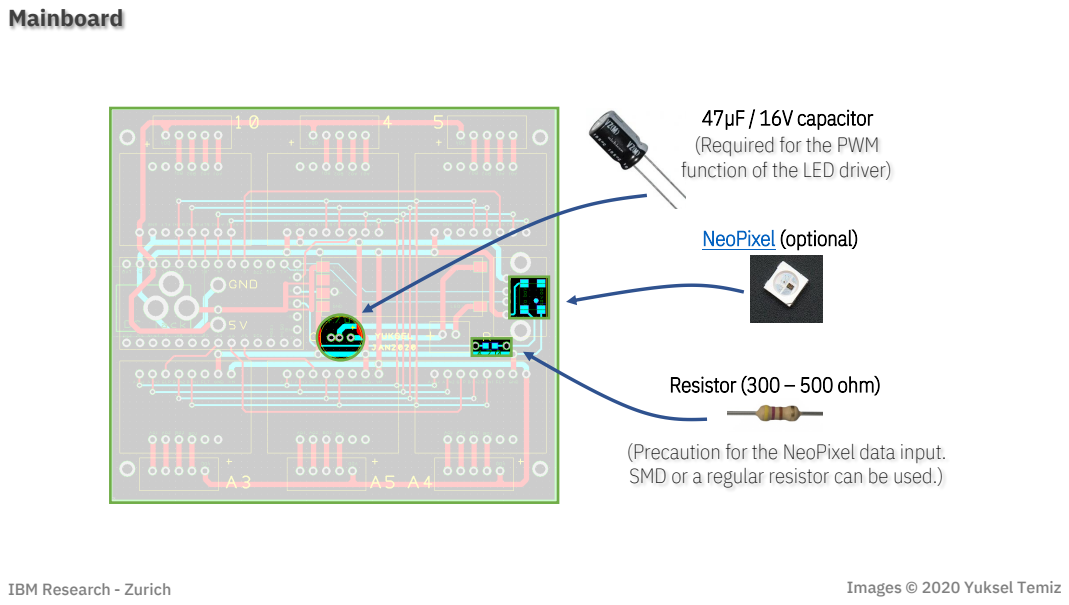
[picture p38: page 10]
NeoPixel (optional); Resistor (300 – 500 ohm)

47µF / 16V capacitor
(Required for the PWM
function of the LED driver)

(Precaution for the NeoPixel data input.
SMD or a regular resistor can be used.)

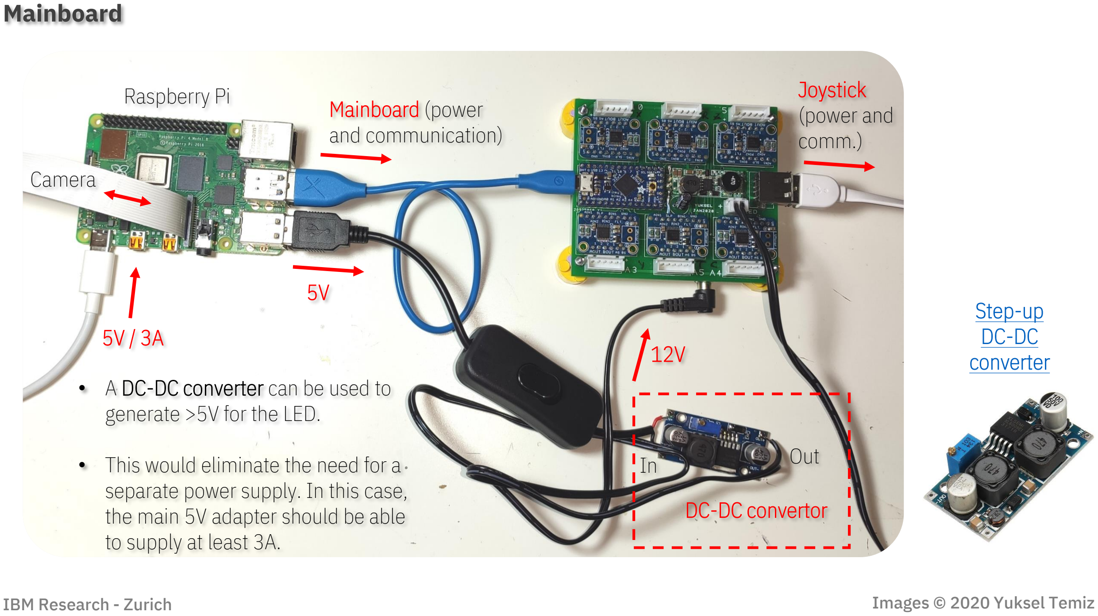
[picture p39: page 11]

5V / 3A

Mainboard (power
and communication)

Camera

5V

12V

DC-DC convertor

- A DC-DC converter can be used to generate >5V for the LED.
- This would eliminate the need for a separate power supply. In this case, the main 5V adapter should be able to supply at least 3A.

Step-up
DC-DC
converter (https://www.banggood.com/DC-DC-Boost-Buck-Adjustable-Step-Up-Step-Down-Automatic-Converter-XL6009-Module-p-1087346.html?rmmds=search&cur_warehouse=CN)

Joystick
(power and
comm.)
In | Out

Raspberry Pi

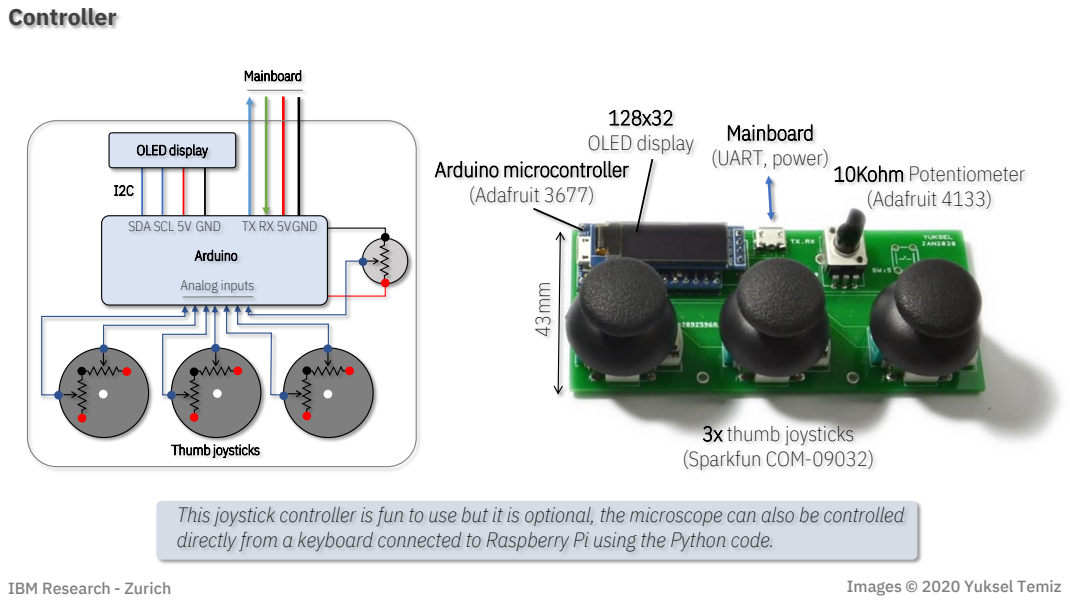
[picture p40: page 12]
Controller; 3x thumb joysticks (Sparkfun COM-09032); 10Kohm Potentiometer (Adafruit 4133); 128x32 OLED display Arduino microcontroller (Adafruit 3677); Mainboard (UART, power); Mainboard; Thumb joysticks; OLED display; SDA SCL; Arduino; 5V GND; GND; Analog inputs

This joystick controller is fun to use but it is optional, the microscope can also be controlled
directly from a keyboard connected to Raspberry Pi using the Python code.

IBM Research - Zurich

Images © 2020 Yuksel Temiz

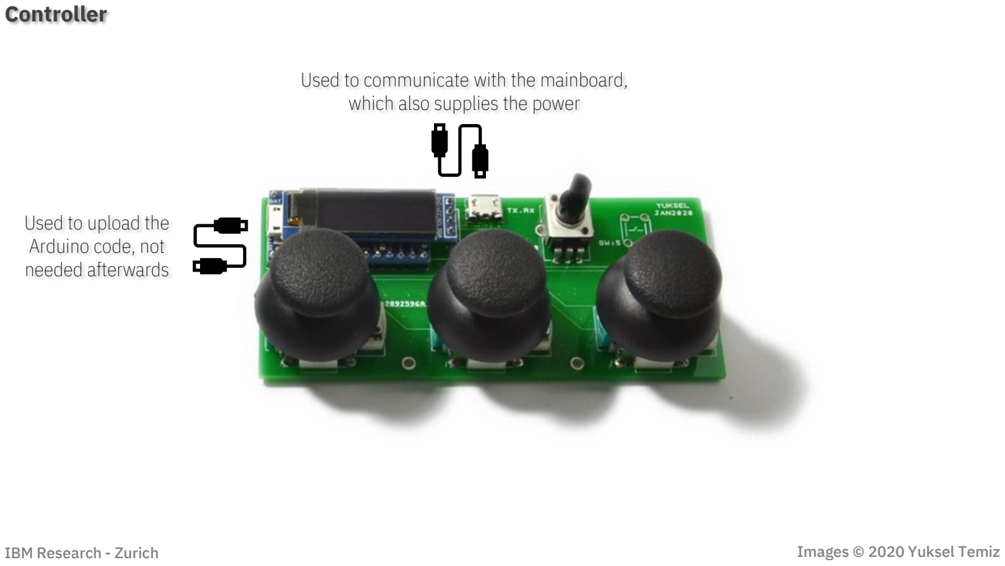
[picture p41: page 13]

Controller

Used to upload the
Arduino code, not
needed afterwards

Used to communicate with the mainboard, which also supplies the power

Controller

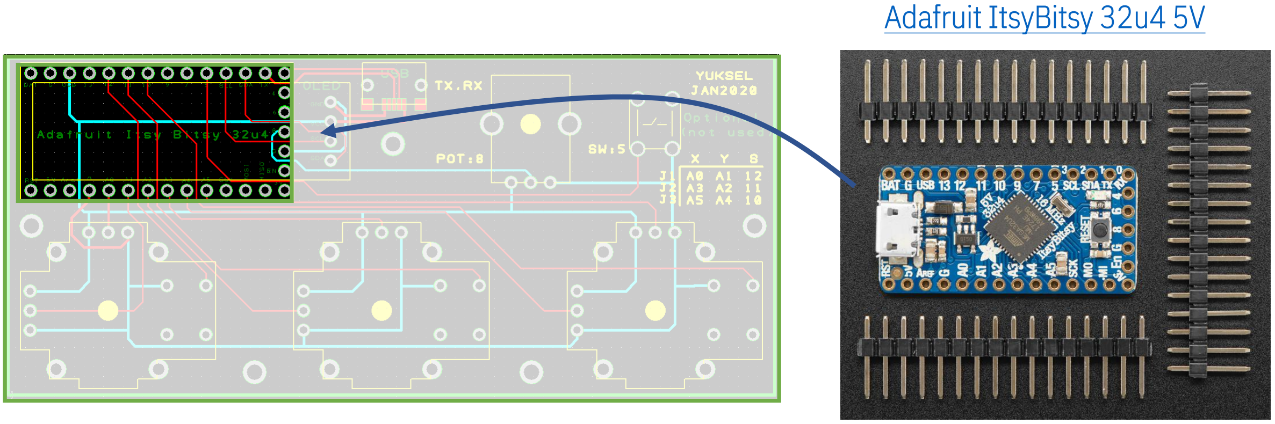
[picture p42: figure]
Adafruit ItsyBitsy 32u4 5V

Controller

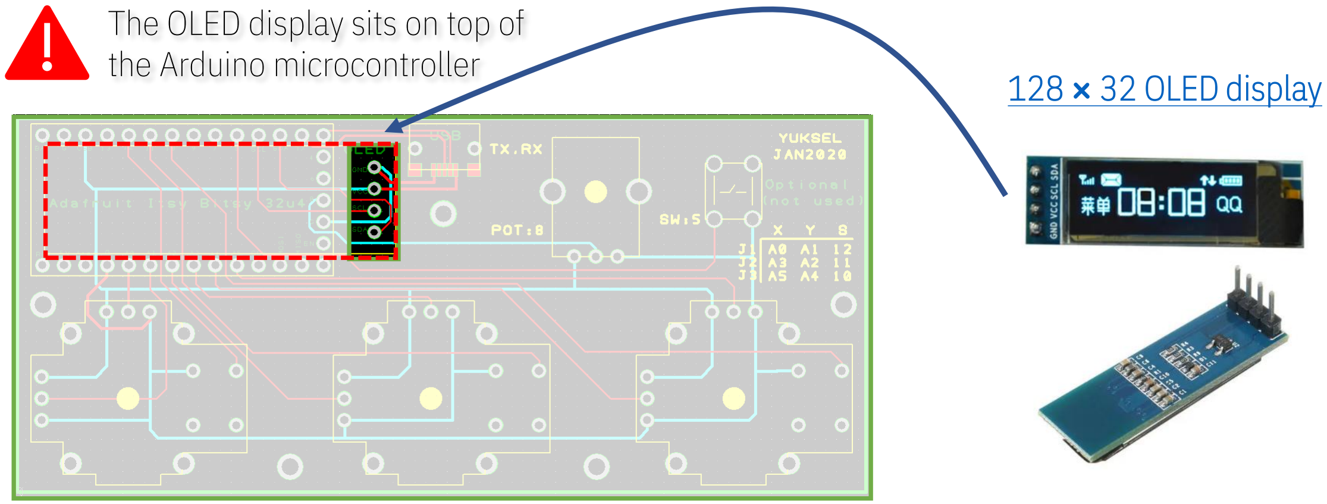
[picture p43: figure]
128 × 32 OLED display; The OLED display sits on top of the Arduino microcontroller
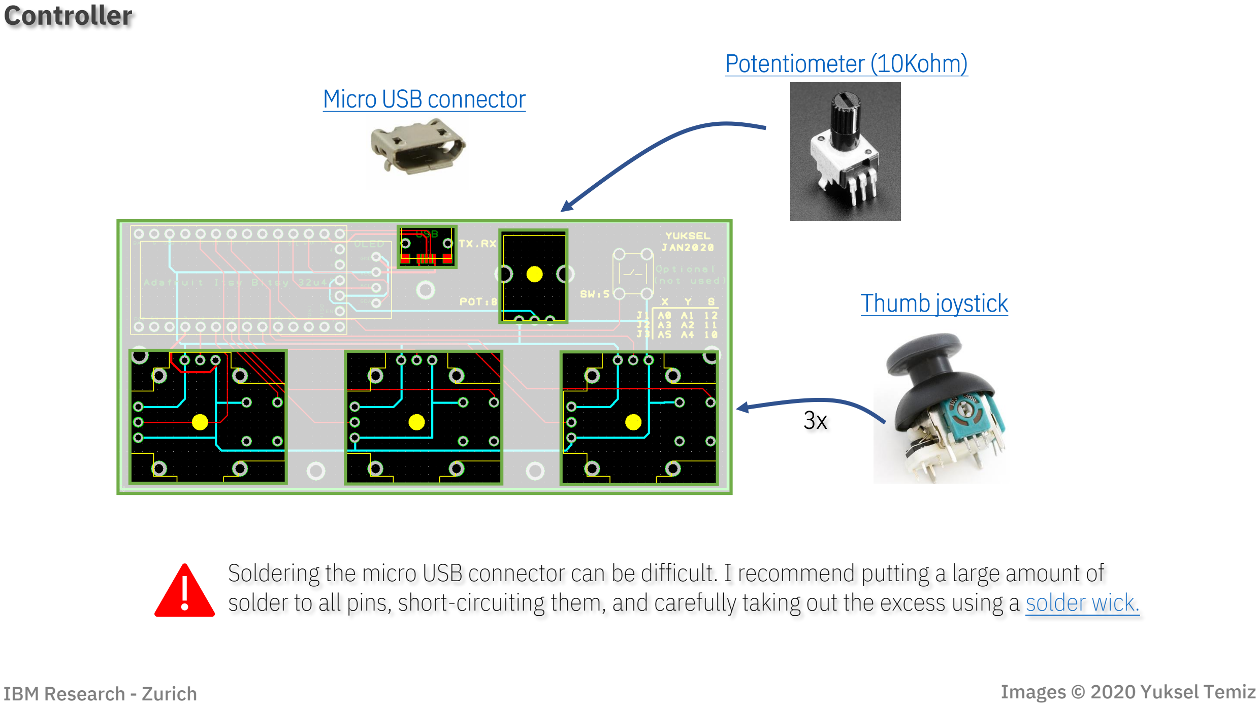
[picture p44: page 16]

Controller

Thumb joystick (https://www.sparkfun.com/products/9032)

3x

Potentiometer (10Kohm) (https://www.adafruit.com/product/4133)
Micro USB connector (https://www.digikey.com/products/en?keywords=609-4616-1-ND)

Soldering the micro USB connector can be difficult. I recommend putting a large amount of solder to all pins, short-circuiting them, and carefully taking out the excess using a solder wick. (https://www.banggood.com/3mm-Desoldering-Braid-Solder-Remover-Wick-Wire-p-982682.html?rmmds=buy&ID=6284394&cur_warehouse=CN)

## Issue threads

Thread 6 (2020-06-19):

### ISSUE TITLE
stacking photo ?

### ISSUE THREAD

**Issue by dimgod59** [IBM/MicroscoPy#6]
hi, 
can we stack the photos? to have a better image depth

**Comment by yukseltemiz** [comment]
Hi, I think it's possible and would be useful. Thanks for the suggestion, I thought about this before, in principle we can slowly change the focus and capture images, I know there are several algorithms available in Python, it's not my area of expertise but I can give it a try and update the repo.

**Comment by thalesfsp** [comment]
@yukseltemiz That would be great! By the way, it's such a great and important (giving the current world situation) project! Congrats for the team that worked on that!

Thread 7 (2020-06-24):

### ISSUE TITLE
BoM and lenses

### ISSUE THREAD

**Issue by thalesfsp** [IBM/MicroscoPy#7]
Hello, :) It would be great if the project had a BoM (Bill of Materials), with links (to the recommended items), and specifications. This would help, and make it easier for people to buy the required items and do the project. Regarding the lenses, what other options do you recommend (high-quality ones) besides the [TREEYE 15.3mm lens M12](https://www.aliexpress.com/i/32879460954.html)? What other lens do you recommend for the HQ-camera? Cheers!

**Comment by yukseltemiz** [comment]
Hi. Thanks for the suggestion. I have a detailed BoM with the weblinks but it was in the long instruction manual, page #71 https://github.com/IBM/MicroscoPy/blob/master/Instructions.pdf

I just added it to the main page  as well. https://github.com/IBM/MicroscoPy/blob/master/Bill%20of%20Materials%20(BOM).pdf

I did not test any other lens with this microscope. [Thorlabs ](https://www.thorlabs.com/navigation.cfm?guide_id=2027) for example have good microscope lenses but they could be too heavy for the tilting stage. Or you could try something like [this,](https://www.banggood.com/HAYEAR-5X-120X-Industrial-Zoom-Lens-for-Digital-Microscope-Camera-C-Mount-Lens-with-High-Working-Distance-p-1449515.html?rmmds=search&cur_warehouse=CN) the HQ camera has a C mount adapter, so you should be able to connect directly.

**Comment by hucik14** [comment]
@thalesfsp have you tried any better lens? I have exactly the same as in the description of this project and I would like to achieve even higher magnification. I wonder how would this one work - [https://www.aliexpress.com/item/32818045696.html](https://www.aliexpress.com/item/32818045696.html) - but I'm afraid that 2 megapixel resolution might be a problem, but maybe not - it is glass so the number is maybe related more to quality than to actual resolution of a lens.

**Comment by yukseltemiz** [comment]
Hi,

Thanks for your message. 

No, I haven't tried a better lens but I've tried Raspberry Pi's HQ camera, 
https://github.com/IBM/MicroscoPy/tree/master/HQ-camera

I had better resolution and color reproducibility with the HQ camera, so 
maybe you can gain a little bit of additional magnification by digital 
zooming, but I think it wouldn't be too significant.

I am aware of this X megapixel spec on these M12 lenses but honestly I 
don't know what it represents. I don't have much (or any) experience in 
optics, this project was a hobby for me. 

You may consider better quality lenses from Thorlabs or Edmund Optics, 
etc. maybe.

Sorry that I couldn't help much.

Best regards,
Yuksel

--------------------------------------------------------------------------------
Yuksel Temiz, Ph.D.
Research Staff Member, Precision Diagnostics
IBM Research - Zurich
Phone: (+41 44) 724 8063 
https://www.zurich.ibm.com/st/precision_diagnostics/

**Comment by hucik14** [comment]
Hi, thank you for your reply :)) the Thorlabs and Edmund Optics lenses looks so good but a bit over budget 😄 I will probably try some lens as I posted before. If I get any results I will share it here.

**Comment by dematoine** [comment]
@hucik14 did you try any of the lenses above? Could you update us with the results? :)

**Comment by hucik14** [comment]
I haven't tried anything different so far, but I still plan to... hopefully I will have time during Christmas holidays. If I have any (even bad) results, I will share it here.

**Comment by harundurmush** [comment]
Hi, can you provide me the references for your optical system? Or an explanation for why did we take the Raspberry Pi camera's lens out?

**Comment by hucik14** [comment]
You remove the original lens and put an external one in bigger distance. Read more on _extension tubes in macro photography_, for example here: 
https://shuttermuse.com/ultimate-guide-to-extension-tubes/

**Comment by hucik14** [comment]
> I haven't tried anything different so far, but I still plan to... hopefully I will have time during Christmas holidays. If I have any (even bad) results, I will share it here.

Sorry I forgot to comment on this - I tried a better lenses, the quality of the images improved a bit, but I was not able to get higher zoom.

**Comment by harundurmush** [comment]
Thanks for your help :)

**Comment by yukseltemiz** [comment]
Hi. I am the designer of the microscope, but I left IBM a few years ago, so the repository is not maintained anymore. 

Regarding the question about the lens, I agree with the previous user's reply. 

I will do my best to answer other questions but it's been a while, I may not remember all the details :-)

**Comment by harundurmush** [comment]
Thank you for your return. I think the instructions are very enough to actualize the project, with all my respect. I am just having a hard time about recreating an alternative version of the optical part, specifically about enough magnification for medical histology.

**Comment by yukseltemiz** [comment]
Thanks. Achieving higher magnification with this single lens configuration can be difficult, and anyway, the resolution will be limited by diffraction. I founded my own company on microscopy, please feel free to check and contact me to learn more: https://www.microqubic.com/ Best regards.

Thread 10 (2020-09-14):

### ISSUE TITLE
Mainboard, mystery component?

### ISSUE THREAD

**Issue by kawong22** [IBM/MicroscoPy#10]
Hello.
I'm looking at the Instructions.pdf page Electronics - Mainboard.  On the picture of the Mainboard, there is an unlabeled black capacitor(?) on the Mainboard to the left of the LED driver.  Does this component need to be soldered on?  What is it and its specifications?  Do you have a part number for it? 
Thank you!
Keith

**Comment by yukseltemiz** [comment]
Hi Keith, sorry I saw your message just now. I had a separate pdf file explaining more details about the electronics: https://github.com/IBM/MicroscoPy/blob/master/Circuit/CircuitAssembly.pdf 

I think the answer should be there but briefly that capacitor is needed for the PWM function of the LED driver. It's in the datasheet of the driver. https://recom-power.com/pdf/Lightline_DC-DC/RCD-24_PL.pdf 

Let me know if this does not help. 
Best,
Yuksel

**Comment by kawong22** [comment]
Thanks! got it.  somehow missed that doc.

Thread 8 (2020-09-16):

### ISSUE TITLE
Information for printing PCBs

### ISSUE THREAD

**Issue by jtabernik** [IBM/MicroscoPy#8]
I am trying to get a quote for printing the PCBs.  Unfortunately, I don't know much about PCBs so the options are very confusing to me (layer count, material type, FR4-TG, thickness, finished copper, min spacing, min hole size, surface finish, etc. etc.--example from a vendor is attached).

Is there somewhere I can get more information to answer these questions for a PCB printing service?  Also, if you or someone else can supply me with the correct responses, I can document this for your project so others will know what to do as well.

Thank you so much for sharing your knowledge on this!  Not only an amazing project, the final result will be incredibly useful!  Thank you!

![image](https://user-images.githubusercontent.com/412300/90944230-75b77b00-e3eb-11ea-98d1-26107f67cbea.png)

**Comment by yukseltemiz** [comment]
Hi, really sorry for my late response, I was on holidays and then didn't see your message. I hope it's not too late but https://jlcpcb.com/ is a good one. Just use everything default, upload the Gerber zip files (https://github.com/IBM/MicroscoPy/tree/master/Circuit) and that's it. I think the system calculates the dimensions and the rest automatically, they will check your design and start the manufacturing, it should cost a few dollars for 5-10 units + shipping.  I used the exact files for my prototypes, so should be fine. Please let me know if it does not work. Thank you for your nice comments and again apologies for being late to respond. Best regards. Yuksel

**Comment by jtabernik** [comment]
No problem and thank you so much!!!!

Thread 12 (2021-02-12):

### ISSUE TITLE
Digital Zoom Moves Off The Screen

### ISSUE THREAD

**Issue by mylesebrown** [IBM/MicroscoPy#12]
Hello.  This project is incredible!  Thank you so much for doing the design work and making it all available here.  I have printed all of my parts with my Prusa i3 MK3S+ printer, ordered the PCB boards and soldered everything up.  I took my time and great care.  When I loaded all the software and turned it on for the first time, it worked!!  Amazing and gratifying.

That said, I have an issue I am encountering that I'd like to discuss and wonder if anyone has thoughts about how to solve this. When I zoom in with the digital zoom, the picture goes off the screen.  Is there any advice about how to solve this?  Is there a software fix that might center it?  I fear that the cause of this issue might be that the camera lens and the Raspberry Pi v2 camera are just slightly misaligned, in which case a software fix wouldn't help.  

I'll post my pictures here.  I am still learning how to position the camera and lens to achieve macro and microscopy.  I have not yet been able to create the beautiful full screen pictures that are shown in the Instruction Manual and on this GitHub
![IMG_0598](https://user-images.githubusercontent.com/74396430/107157814-1f0f1080-693b-11eb-8b69-c0770e8c1d9b.jpg)
![IMG_0597](https://user-images.githubusercontent.com/74396430/107157815-20403d80-693b-11eb-9adf-d3c18b3ab372.jpg)
![IMG_0596](https://user-images.githubusercontent.com/74396430/107157816-20d8d400-693b-11eb-80ef-c641fbc08ee0.jpg)
![IMG_0595](https://user-images.githubusercontent.com/74396430/107157823-29310f00-693b-11eb-9eae-1bed4a1c0064.jpg)
![IMG_0594](https://user-images.githubusercontent.com/74396430/107157824-2afad280-693b-11eb-8eae-0d07e430ce22.jpg)
![IMG_0593](https://user-images.githubusercontent.com/74396430/107157825-2cc49600-693b-11eb-8d9f-f5f1f0369218.jpg)
![IMG_0592](https://user-images.githubusercontent.com/74396430/107157826-2e8e5980-693b-11eb-837b-aeb69ba3a5e3.jpg)
![IMG_0591](https://user-images.githubusercontent.com/74396430/107157827-30581d00-693b-11eb-9861-c134a857d6b4.jpg)
![IMG_0590](https://user-images.githubusercontent.com/74396430/107157828-31894a00-693b-11eb-87c8-2192ab187390.jpg)
![07-02-113538](https://user-images.githubusercontent.com/74396430/107157839-3817c180-693b-11eb-9534-b82a6872171c.jpg)
![07-02-113534](https://user-images.githubusercontent.com/74396430/107157841-3948ee80-693b-11eb-9aeb-ee916a20974b.jpg)
![07-02-113526](https://user-images.githubusercontent.com/74396430/107157842-3b12b200-693b-11eb-9e7a-de25cf7b1689.jpg)
![Uploading 07-02-113521.jpg…]()

**Comment by yukseltemiz** [comment]
Hello, wow, looks great, beautiful implementation, I am very glad that you liked the project and implemented it. 

1- Yes, there is certainly an issue, I am guessing (almost certain) that maybe you forgot to remove the built-in lens of the Pi camera v2(?). Because we already have a magnifying lens, the tiny lens in front of the camera should be removed so that the lens directly projects to naked CMOS imager. Please check page 15 of the instructions pdf, it's explained at the bottom right corner, super easy, just unscrew it (I should have emphasized it better, it's a very important step). 

2- Regarding the digital zoom, when you have the microscope properly running (either the lens issue or something else), you will see that you won't even need the digital zoom, you will be amazed by the magnification level :-) But still, the digital zoom currently magnifies the top-left corner of the image, I could have centered but that would be quite some programming, I didn't have time. 

3- Just as a general comment, the respective distances between the image sensor, lens, and the sample define the magnification and the focus. For low magnification, move the camera closer to the lens, and increase the distance between the lens and the sample; for high magnification, exactly the opposite. Based on my experience, you should be able to see the whole insect in low magnification, and the individual cells in its eyes in high magnification. For high magnification, the illumination would be very important, you may also try to illuminate the sample from the top.

I hope this helps, otherwise just let me know. All the best.

**Comment by mylesebrown** [comment]
Wow! Thank you so much for your reply Yuksel!  I did indeed forget to remove the built in lens of the Pi camera.  This was exactly the problem.  The microscope is now performing beautifully!  

I have always wanted to learn about Raspberry Pi and Arduinos.  This is my first attempt.  I can't believe that nearly everything worked so perfectly on the first try except for my mistake about removing the lens.  I look forward to working more with this microscope and teaching my kids more about the technology as well as some good biology lessons.  Next, I will try to get more advanced with the lighting as you suggest.

Also, I have some ideas about upgrades/improvements that I will figure out how to post on this project page if you are ok with that?

Thank you again for sharing your talent with the world!!
Myles, 
Seattle, WA  USA

![Moth Eye High Zoom](https://user-images.githubusercontent.com/74396430/107687276-22680c00-6c5b-11eb-9606-480ab30950a7.jpg)
![Moth Antenna High Zoom](https://user-images.githubusercontent.com/74396430/107687279-2431cf80-6c5b-11eb-9a6c-3fe4f66b1738.jpg)
![Dead Moth Low Zoom](https://user-images.githubusercontent.com/74396430/107687284-2562fc80-6c5b-11eb-8286-18ecde2e8d8b.jpg)

**Comment by yukseltemiz** [comment]
This is great, thanks Myles for sharing the results and for your kind comments! I am also very impressed that you pulled everything off without much prior experience on Pi and Arduino, amazing.   

(Just one side note, you may have noticed some purple tint in the images, especially at the corners, this is because Pi camera v2 does not have an IR filter. The lens you bought probably has a filter, but it does not help much because the lens is often far from the camera in higher magnifications and the angle of incidence is not optimal, ideally the filter should be close to the camera, at least this is my interpretation... anyhow, this can be corrected by some post-processing, or I got much better results with the new HQ camera, which has a built-in IR filter: https://github.com/IBM/MicroscoPy/blob/master/HQ-camera/Instructions_HQ.pdf)

For the improvements and sharing, of course, sounds great. This was mostly a hobby project for me, and I guess we shouldn't expect too much from cheap optics but I am pretty sure there is plenty of room for improvements, this was also one of the reasons we wanted to open-source, so others can implement and improve. Looking forward to seeing your suggestions/improvements. 

Thanks, best regards,
Yuksel

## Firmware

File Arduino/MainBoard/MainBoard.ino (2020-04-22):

/* This code controls the stepper motors and the LED intensity
 * according to the data received from the UART (RX, TX) (Controller) or the USB (e.g. Raspberry Pi)
 * All 6 motors share the same stepper motor pins, but only one
 * is activated depending on the status of the Enable pin of the driver
 * Data format: "50X," where 50 is the speed and X is the axis
 * X: X axis, Y: Y axis, Z: Z axis, C: camera stage, R: rotation, T: tilt 
 * The data is executed after a "," (comma) is received
 */

// Arduino board: Adafruit ItsyBitsy32u4 5V 

#include <AccelStepper.h> // Library to control stepper motors // Copyright (C) 2010-2018 Mike McCauley

AccelStepper myStepper(AccelStepper::FULL4WIRE, 12, 9, 11, 7); // stepper motor pins

#include <Adafruit_NeoPixel.h> // Library to control the optional status LED

////////////////// Arduino pins connected to the EN of each stepper motor driver

#define EnableX 10
#define EnableY A3
#define EnableZ 5
#define EnableC A4
#define EnableR 4
#define EnableT A5

/////////////////

#define LEDPWM 6 // High-power illumination LED PWM control pin
#define NeopixelPin 8 // # Status LED (optional, not used)

const int stepsPerRevolution = 2048; //set according to the specs of the stepper motor
String receivedString; //incoming data from the serial ports (USB or UART)
int stepperSpeed;
char state; //variable to define the active stepper motor, X, Y, Z, C, R, T
int LEDintensity;

Adafruit_NeoPixel pixel(1, NeopixelPin, NEO_GRB + NEO_KHZ800);


void setup() {

  Serial1.begin(57600); // UART with the jostick controller
  Serial.begin(57600); // USB, Raspberry Pi
  
  pinMode(EnableX, OUTPUT);
  pinMode(EnableY, OUTPUT);
  pinMode(EnableC, OUTPUT);
  pinMode(EnableZ, OUTPUT);
  pinMode(EnableR, OUTPUT);
  pinMode(EnableT, OUTPUT);
  pinMode(LEDPWM, OUTPUT);

  analogWrite(LEDPWM, 255); // initialize the LED intensity to 0% 
  /* PWM of the LED driver (RCD-24-0.70/PL/B, Recom) used in this project
   * works in the opposite direction, i.e. 255 is for 0% and 0 for 100% intensity
   */
  
  pixel.begin();
  pixel.setPixelColor(0, pixel.Color(0, 0, 50));
  pixel.show();
  
  myStepper.setMaxSpeed(1000);
}

void loop() {

////// data from UART: joystick controller

  if (Serial1.available() > 0) {
    char data = Serial1.read();
    if (data == ',') { // receive data until "," is received

      if (receivedString.length() > 1) {
        int stepperSpeed = receivedString.toInt(); // convert the motor speed information to an integer
        myStepper.setSpeed(stepperSpeed); // set the speed
        
        if (receivedString.indexOf('X') > 0) { //X axis
          state = 'X';
        }
        if (receivedString.indexOf('Y') > 0) { //Y axis
          state = 'Y';
        }
        if (receivedString.indexOf('C') > 0) { //Camera stage
          state = 'C';
        }

        if (receivedString.indexOf('Z') > 0) { //Z axis
          state = 'Z';
        }

        if (receivedString.indexOf('R') > 0) { //Rotation stage
          state = 'R';
        }

        if (receivedString.indexOf('T') > 0) { //Tilting mechanism
          state = 'T';
        }

        if (receivedString.indexOf('L') > 0) { //LED
          LEDintensity = map(stepperSpeed, 0, 20, 0, 255); //map to a number from 0 to 255
          analogWrite(LEDPWM, LEDintensity);
        }

        if (receivedString.indexOf('O') > 0) { //Disable all stepper motors
          state = 'O';
        }
        receivedString = ""; //reset the string for the next incoming data
      }
    }
    else {
      receivedString += data; //store the incoming data in a string until "," is received (above)
    }
  }

//// data from USB (Raspberry Pi) (same as above but Serial instead of Serial1)

  if (Serial.available() > 0) {
    char data = Serial.read();
    if (data == ',') {

      if (receivedString.length() > 1) {
        int stepperSpeed = receivedString.toInt();
        myStepper.setSpeed(stepperSpeed);
        if (receivedString.indexOf('X') > 0) {
          state = 'X';
        }
        if (receivedString.indexOf('Y') > 0) {
          state = 'Y';
        }
        if (receivedString.indexOf('C') > 0) {
          state = 'C';
        }

        if (receivedString.indexOf('Z') > 0) {
          state = 'Z';
        }

        if (receivedString.indexOf('R') > 0) {
          state = 'R';
        }

        if (receivedString.indexOf('T') > 0) {
          state = 'T';
        }

        if (receivedString.indexOf('L') > 0) {
          LEDintensity = map(stepperSpeed, 0, 20, 0, 255);
          analogWrite(LEDPWM, LEDintensity);
        }

        if (receivedString.indexOf('O') > 0) {
          state = 'O';
        }
        receivedString = "";
      }
    }
    else {
      receivedString += data;
    }
  }

///// RUN STEPPER MOTORS, only one runs at a given time

  if (state == 'X') {

    digitalWrite(EnableX, HIGH);
    myStepper.runSpeed();
  }

  if (state == 'Y') {

    digitalWrite(EnableY, HIGH);
    myStepper.runSpeed();
  }

  if (state == 'C') {

    digitalWrite(EnableC, HIGH);
    myStepper.runSpeed();
  }

  if (state == 'Z') {

    digitalWrite(EnableZ, HIGH);
    myStepper.runSpeed();
  }

  if (state == 'R') {

    digitalWrite(EnableR, HIGH);
    myStepper.runSpeed();
  }

  if (state == 'T') {

    digitalWrite(EnableT, HIGH);
    myStepper.runSpeed();
  }

// TURN OFF all stepper motors 

  if (state == 'O') {
    digitalWrite(EnableX, LOW);
    digitalWrite(EnableY, LOW);
    digitalWrite(EnableZ, LOW);
    digitalWrite(EnableC, LOW);
    digitalWrite(EnableR, LOW);
    digitalWrite(EnableT, LOW);
  }

}

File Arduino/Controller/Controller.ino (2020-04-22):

/* This code sends data via UART from one Arduino board (controller) to another (MainBoard) to control the stepper motors and the LED illumination
 * Arduino sends the data only if there is a change in the value of the joysticks or the LED potentiometer 
 * Therefore, there is no continuous data communication between the mainboard and the controller
 * Arduino board: Adafruit ItsyBitsy 32u4 5V  
 */

#include <Wire.h> // needed for the I2C communication of the OLED, already installed in Arduino IDE
#include <Adafruit_GFX.h> // needed for the OLED // Copyright (c) 2012 Adafruit Industries.  All rights reserved.
#include <Adafruit_SSD1306.h> // needed for the OLED // Copyright (c) 2012 Adafruit Industries.  All rights reserved.

// Arduiono pins for the joysticks
#define joystickX A0
#define joystickY A1
#define joystickC A3
#define joystickZ A2
#define joystickR A5
#define joystickT A4

// potentiometer for the LED intensity
#define potLED 8


// change these values to set the direction of the movement with respect to the joystick
// the direction can also be changed by simply rotating the motor 180-deg 

#define directionX -1
#define directionY 1
#define directionZ 1
#define directionC 1
#define directionR -1
#define directionT 1

// the joystick has a variable speed control at 3 predefined speeds
// change these values to change the speed of the motor

#define fast 500
#define medium 50
#define slow 10

#define SCREEN_WIDTH 128 // OLED display width, in pixels
#define SCREEN_HEIGHT 32 // OLED display height, in pixels
Adafruit_SSD1306 display(SCREEN_WIDTH, SCREEN_HEIGHT, &Wire);

int readX;
int readY;
int readC;
int readZ;
int readR;
int readT;
int readL;

int readXlast = 0;
int readYlast = 0;
int readClast = 0;
int readZlast = 0;
int readRlast = 0;
int readTlast = 0;
int readLlast = 0;

String stepper;

void setup() {

  display.begin(SSD1306_SWITCHCAPVCC, 0x3c); //initialize the display
  Serial1.begin(57600); //start the serial communication, Serial1: UART

  pinMode(joystickX, INPUT);
  pinMode(joystickY, INPUT);
  pinMode(joystickZ, INPUT);
  pinMode(joystickC, INPUT);
  pinMode(joystickR, INPUT);
  pinMode(joystickT, INPUT);
  pinMode(potLED, INPUT);

// show a start-up text on the OLED display

  display.clearDisplay();
  display.setRotation(2);
  display.setTextColor(WHITE);
  display.setCursor(0, 10);
  display.setTextSize(2);
  display.println("Welcome!");
  display.display();

  delay(2000); //optional delay for the start-up message

// set the LED illumination to the potentiometer value at the start-up

  readLlast = map((analogRead(potLED)), 0, 1023, 0, 20); // map to 20 steps (5% steps) 
  Serial1.print(readL); Serial1.print("L"); Serial1.print(","); // send the data to the MainBoard to update the LED intensity
  
// show the LED intensity on the OLED display

  display.clearDisplay();
  display.setCursor(0, 10);
  display.setTextSize(2);
  display.print("LED:"); display.print(100 - (readLlast * 5)); display.print("%"); // PWM of the LED driver used in the prototype works in the opposite direction
  display.display();

}

void loop() {

  readX = map((analogRead(joystickX)), 0, 1023, -3, 3); // map the measured value to 3 positive and 3 negative speed values
  if ((readX != readXlast) ) { //check if it has changed
    if (readX == -3) {
      Serial1.print(fast * -1 * directionX); Serial1.print("X"); Serial1.print(",");
      readXlast = readX;
    }
    if (readX == -2)  {
      Serial1.print(medium * -1 * directionX); Serial1.print("X"); Serial1.print(",");
      readXlast = readX;
    }
    if (readX == -1)  {
      Serial1.print(slow * -1 * directionX); Serial1.print("X"); Serial1.print(",");
      readXlast = readX;
    }
    if (readX == 0) {
      Serial1.print(0); Serial1.print("O"); Serial1.print(","); //stop the stepper motor by sending "0O,"
      readXlast = readX;
    }
    if (readX == 1)  {
      Serial1.print(slow * directionX); Serial1.print("X"); Serial1.print(",");
      readXlast = readX;
    }

    if (readX == 2)  {
      Serial1.print(medium * directionX); Serial1.print("X"); Serial1.print(",");
      readXlast = readX;
    }

    if (readX == 3)  {
      Serial1.print(fast * directionX); Serial1.print("X"); Serial1.print(",");
      readXlast = readX;
    }

  }

// REPEAT THE SAME FOR ALL OTHER JOYSTICK POTENTIOMETERS 

  readY = map((analogRead(joystickY)), 0, 1023, -3, 3);
  if (readY != readYlast) {
    if (readY == -3)  {
      Serial1.print(fast * -1 * directionY); Serial1.print("Y"); Serial1.print(",");
      readYlast = readY;
    }
    if (readY == -2)  {
      Serial1.print(medium * -1 * directionY); Serial1.print("Y"); Serial1.print(",");
      readYlast = readY;
    }
    if (readY == -1)  {
      Serial1.print(slow * -1 * directionY); Serial1.print("Y"); Serial1.print(",");
      readYlast = readY;
    }
    if (readY == 0) {
      Serial1.print(0); Serial1.print("O"); Serial1.print(",");
      readYlast = readY;
    }
    if (readY == 1)  {
      Serial1.print(slow * directionY); Serial1.print("Y"); Serial1.print(",");
      readYlast = readY;
    }

    if (readY == 2)  {
      Serial1.print(medium * directionY); Serial1.print("Y"); Serial1.print(",");
      readYlast = readY;
    }

    if (readY == 3)  {
      Serial1.print(fast * directionY); Serial1.print("Y"); Serial1.print(",");
      readYlast = readY;
    }

  }

  readC = map((analogRead(joystickC)), 0, 1023, -3, 3);
  if (readC != readClast) {
    if (readC == -3)  {
      Serial1.print(fast * -1 * directionC); Serial1.print("C"); Serial1.print(",");
      readClast = readC;
    }
    if (readC == -2)  {
      Serial1.print(medium * -1 * directionC); Serial1.print("C"); Serial1.print(",");
      readClast = readC;
    }
    if (readC == -1) {
      Serial1.print(slow * -1 * directionC); Serial1.print("C"); Serial1.print(",");
      readClast = readC;
    }
    if (readC == 0)  {
      Serial1.print(0); Serial1.print("O"); Serial1.print(",");
      readClast = readC;
    }
    if (readC == 1)  {
      Serial1.print(slow * directionC); Serial1.print("C"); Serial1.print(",");
      readClast = readC;
    }

    if (readC == 2)  {
      Serial1.print(medium * directionC); Serial1.print("C"); Serial1.print(",");
      readClast = readC;
    }

    if (readC == 3) {
      Serial1.print(fast * directionC); Serial1.print("C"); Serial1.print(",");
      readClast = readC;
    }

  }

  readZ = map((analogRead(joystickZ)), 0, 1023, -3, 3);
  if (readZ != readZlast) {
    if (readZ == -3)  {
      Serial1.print(fast * -1 * directionZ); Serial1.print("Z"); Serial1.print(",");
      readZlast = readZ;
    }
    if (readZ == -2)  {
      Serial1.print(medium * -1 * directionZ); Serial1.print("Z"); Serial1.print(",");
      readZlast = readZ;
    }
    if (readZ == -1)  {
      Serial1.print(slow * -1 * directionZ); Serial1.print("Z"); Serial1.print(",");
      readZlast = readZ;
    }
    if (readZ == 0) {
      Serial1.print(0); Serial1.print("O"); Serial1.print(",");
      readZlast = readZ;
    }
    if (readZ == 1) {
      Serial1.print(slow * directionZ); Serial1.print("Z"); Serial1.print(",");
      readZlast = readZ;
    }

    if (readZ == 2)  {
      Serial1.print(medium * directionZ); Serial1.print("Z"); Serial1.print(",");
      readZlast = readZ;
    }

    if (readZ == 3)  {
      Serial1.print(fast * directionZ); Serial1.print("Z"); Serial1.print(",");
      readZlast = readZ;
    }

  }

  readR = map((analogRead(joystickR)), 0, 1023, -3, 3);
  if (readR != readRlast)  {
    if (readR == -3) {
      Serial1.print(fast * -1 * directionR); Serial1.print("R"); Serial1.print(",");
      readRlast = readR;
    }
    if (readR == -2) {
      Serial1.print(medium * -1 * directionR); Serial1.print("R"); Serial1.print(",");
      readRlast = readR;
    }
    if (readR == -1)  {
      Serial1.print(slow * -1 * directionR); Serial1.print("R"); Serial1.print(",");
      readRlast = readR;
    }
    if (readR == 0) {
      Serial1.print(0); Serial1.print("O"); Serial1.print(",");
      readRlast = readR;
    }
    if (readR == 1)  {
      Serial1.print(slow * directionR); Serial1.print("R"); Serial1.print(",");
      readRlast = readR;
    }

    if (readR == 2)  {
      Serial1.print(medium * directionR); Serial1.print("R"); Serial1.print(",");
      readRlast = readR;
    }

    if (readR == 3) {
      Serial1.print(fast * directionR); Serial1.print("R"); Serial1.print(",");
      readRlast = readR;
    }

  }

  readT = map((analogRead(joystickT)), 0, 1023, -3, 3);
  if (readT != readTlast)  {
    if (readT == -3) {
      Serial1.print(fast * -1 * directionT); Serial1.print("T"); Serial1.print(",");
      readTlast = readT;
    }
    if (readT == -2) {
      Serial1.print(medium * -1 * directionT); Serial1.print("T"); Serial1.print(",");
      readTlast = readT;
    }
    if (readT == -1) {
      Serial1.print(slow * -1 * directionT); Serial1.print("T"); Serial1.print(",");
      readTlast = readT;
    }
    if (readT == 0)  {
      Serial1.print(0); Serial1.print("O"); Serial1.print(",");
      readTlast = readT;
    }
    if (readT == 1)  {
      Serial1.print(slow * directionT); Serial1.print("T"); Serial1.print(",");
      readTlast = readT;
    }

    if (readT == 2)  {
      Serial1.print(medium * directionT); Serial1.print("T"); Serial1.print(",");
      readTlast = readT;
    }
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

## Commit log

2020-04-22 Create Controller housing.FCStd
    [Controller housing.FCStd]
2020-04-22 Create Controller knob.FCStd
    [Controller knob.FCStd]
2020-06-14 Create Bill of Materials (BOM).pdf
2021-03-18 Update Bill of Materials (BOM).pdf
2021-04-29 [ImgBot] Optimize images
    *Total -- 74,381.73kb -> 66,415.87kb (10.71%)
    /Image-examples/Droplets.jpg -- 309.86kb -> 229.57kb (25.91%)
    /docs/Electronics.jpg -- 583.83kb -> 483.77kb (17.14%)
    /docs/Circuit.jpg -- 502.42kb -> 425.47kb (15.32%)
    /HQ-camera/HQ-camera.gif -- 23,608.08kb -> 20,219.60kb (14.35%)
    /docs/Diagram.jpg -- 481.17kb -> 421.15kb (12.47%)
    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
2021-06-04 [ImgBot] Optimize images
    *Total -- 50,773.65kb -> 46,196.27kb (9.02%)
    /docs/Assembly.gif -- 10,709.88kb -> 9,479.43kb (11.49%)
    /docs/Modes.jpg -- 999.51kb -> 887.85kb (11.17%)
    /docs/Animation.gif -- 18,780.41kb -> 16,865.27kb (10.2%)
    /docs/3Dprinting.jpg -- 527.31kb -> 473.95kb (10.12%)
    /docs/Arduino.jpg -- 562.12kb -> 507.88kb (9.65%)
    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
